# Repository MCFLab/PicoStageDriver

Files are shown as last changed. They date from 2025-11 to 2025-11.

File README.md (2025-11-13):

# Welcome to the Pico Stage Driver Project

The **Pico Stage Driver Project** is an open-source development of a low-cost, open-source controller design that drives several stepper motors and implements important safety features, such as monitoring of mechanical limit switches, stall detection, and protective software limits. If rotational encoders in the motors or linear encoders on the stages are available, the controller can monitor the stage position and correct it in a feedback loop. The stages can be controlled with serial commands via USB, or optionally from a remote control box that incorporates a joystick for real-time multi-axis speed control, rotary dials for fine axis positioning, and a display to indicate the stage positions. To ease adoption, we provide driver libraries in Python and C, a driver for the commonly used microscopy control software µManager, and an example graphical user interface for calibration and testing.

## Content

A paper describing the design and implementation is published here:

Mathias S. Fischer, David Grass, and Martin C. Fischer, "Modular multi-axis stepper motor driver with remote control for use in microscopy," [arXiv:2511.09456](https://doi.org/10.48550/arXiv.2511.09456) (2025).

Here we provide the [Bill of Materials](BOM.md), [Assembly Instructions](Assembly.md), and more detailed [Calibration Instructions](Calibration.md) than contained in the publication.

The [Mechanical Drawings](MechanicalDrawings/README.md) and [Software](Software/README.md) are in their respective subdirectories.

## Contributing

We welcome your contributions with [pull-requests](https://github.com/MCFLab/PicoStageDriver/pulls) and [issues suggesting further improvement](https://github.com/MCFLab/PicoStageDriver/issues)!

## License

This work is licensed under the
[GNU General Public License Version 3](https://www.gnu.org/licenses/gpl-3.0.en.html).

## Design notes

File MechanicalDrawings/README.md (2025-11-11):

# Mechanical Drawings

## Motor Controller

For the motor controller, we used an aluminum enclosure (Hammond 1455U2801, see BOM). On the front, we need holes for the USB cable to the Pico, the power switch, and two LEDs. On the back we mounted two rows of 9-pin Sub-D connectors for the motors and encoder/limit switches, the power connector jack, and the connector for the cable to the remote controller. We used a waterjet to cut the holes, using the "Motor Controller Front Panel" and "Motor Controller Back Panel" design files (supplied as Fusion 360 and STEP files). The cable connector is screwed to a 3D-printed adapter piece "RJ45Adapter", which we then glued to the inside of the back plate of the case.

## Remote Controller

The components for the remote controller are mounted in a 3D-printed case, consisting of a top shell and a bottom plate. For modularity, we designed the top shell as an assembly, which contains the shell and inserts for the joystick, the display, and motor controller cable connector. All of the shell components are attached with small #2 self-tapping screws. The encoders and the sensitivity potentiometer have threads and nuts and are fitted into the corresponding holes.

Note that the mounting holes for these components can differ between manufacturers and the dimensions might need adjustments.

We provide the Autodesk Inventor files and STEP files for the remote controller enclosure:

- Inventor:
  - "Top Assembly" (incorporating "RemoteControllerTop", "RJ45Insert", "JoystickInsert", and "DisplayInsert")
  - "RemoteControllerBottom"
- STEP
  - "Top Assembly"
  - "RemoteControllerBottom"

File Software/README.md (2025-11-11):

# Software

We provide the required software to be loaded onto the Motor Controller Pico and, if used, the remote controller Pico. The attached stages can be controlled either through the remote controller (if used) or via serial commands over USB (see the [detailed list of commands](CommandList.md)).

We also offer a driver package to interface with the Pico Stage Driver both in C and in Python, as well as simple graphical user interfaces utilizing these drivers. In addition, we implemented a rudimentary version of a driver for the popular microscopy control software [µManager](https://micro-manager.org/).

We provide basic [installation instructions](SoftwareInstallation.md) for all of the software provided.

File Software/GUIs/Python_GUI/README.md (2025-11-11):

# Stage Driver GUI

Small Tkinter GUI used to interact with PicoStage hardware. The
repository contains a lightweight MVC split: `stage_driver_view` for the
UI, `stage_driver_controller` for logic and `picostage` (external) for
hardware access.

What is included

- `panel_controls.py`, `status_panel.py`, `input_history_panel.py` — UI
  widgets and small controls.
- `stage_driver_view.py` — the main application window (Panel).
- `stage_driver_controller.py` — controller that wires the Panel to the
  PicoStage backend.
- `logging_texthandler.py` — helper that routes logging messages to the
  UI.

Quick start (development)

1. Create or activate a Python environment (this project was developed
   with Python 3.8+).

2. Run the GUI (requires the PicoStage package and hardware or a mock):

```powershell
py -3 main.py
```

Notes

- The GUI code uses tkinter widgets; tests instantiate widgets headless
  (no mainloop) and should run on systems with tkinter available.
- If your environment does not have `py` launcher, use your `python`
  executable instead.

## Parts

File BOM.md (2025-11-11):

# Bill of Materials

Note: Prices are approximate as of Nov 2025

## Motor Controller

| **Component** | **Number** | **Cost / unit** | **Source** | **Part number** | **Link** |
|----------|------|------|-------|--------|-------------------------------------|
| Microcontroller | 1 | \$5 | Raspberry Pi | Pico 2 | <https://www.raspberrypi.com/products/raspberry-pi-pico-2/> |
| TMC eval boards | 1-4 | \$68 | Analog Devices | TMC5240-EVAL | <https://www.analog.com/en/products/tmc5240.html> |
| Box | 1 | \$50 | Hammond | 1455U2801 | <https://www.newark.com/hammond/1455u2801/enclosure-multipurpose-extruded/dp/31AJ8269> |
| Power switch | 1 | \<\$1 | E-Switch | RA1113112R | <https://www.digikey.com/en/products/detail/e-switch/RA1113112R/3778055> |
| Power Jack | 1 | \$2 | MPD | EJ501B | <https://www.digikey.com/en/products/detail/mpd-memory-protection-devices/EJ501B/2439533> |
| Sub-D conn (female) | 1-4 | \<\$1 | various | A-DF 09 LL/Z | <https://www.digikey.com/en/products/detail/assmann-wsw-components/A-DF-09-LL-Z/5051922> |
| Sub-D conn (male) | 1-4 | \<\$1 | various | A-DS 09 LL/Z | <https://www.digikey.com/en/products/detail/assmann-wsw-components/A-DS-09-LL-Z/1241781> |
| Sub-D jack screws | 2-8 | \<\$1 | various | 4750-3 | <https://www.digikey.com/en/products/detail/raf-electronic-hardware/4750-3/7681452> |
| Protoboard | 1 | \$5 | Adafruit | 1609 | <https://www.adafruit.com/product/1609> |
| Headers for TMC board | 1-4 | \<\$1 | various | 10129381-950002BLF | <https://www.digikey.com/en/products/detail/amphenol-cs-fci/10129381-950002BLF/7916116> |
| RJ Jack | 1 | \$3 | Same Sky | CRJ068-1-SMT | <https://www.digikey.com/en/products/detail/same-sky-formerly-cui-devices/CRJ068-1-SMT/14322791> |
| Screw terminals | 2 | \$1 | Adels-Contact | 230/ 5 DS | <https://www.digikey.com/en/products/detail/adels-contact/230-5-DS/9998591> |
| 5-pin wire connectors (5-pack) | 1 | \$8 | Fielect |  | <https://www.amazon.com/dp/B0819PX1GY/> |
|  |  |  |  |  |  |

## Remote Controller

| **Component** | **Number** | **Cost / unit** | **Source** | **Part number** | **Link** |
|----------|------|-----|-------|--------|-------------------------------------|
| Microcontroller | 1 | \$5 | Raspberry Pi | Pico 2 | <https://www.raspberrypi.com/products/raspberry-pi-pico-2/> |
| Protoboard | 1 | \$5 | Adafruit | 1609 | <https://www.adafruit.com/product/1609> |
| RJ Jack | 1 | \$3 | Same Sky | CRJ068-1-SMT | <https://www.digikey.com/en/products/detail/same-sky-formerly-cui-devices/CRJ068-1-SMT/14322791> |
| Joystick | 1 | \$6 | Adafruit | 512 | <https://www.adafruit.com/product/512> |
| Rotary dial encoders | 1-4 | \$2 | various | KY-040 | <https://www.amazon.com/dp/B0D2TVTC75/> |
| Potentiometer | 1 | \$1 | various |  | <https://www.digikey.com/en/products/detail/tt-electronics-bi/P110KH1-0F15BR10K/2408866> |
| Knob for pot | 1 | \<\$1 | various |  | <https://www.digikey.com/en/products/detail/same-sky-formerly-cui-devices/SPK-016C/26004447> |
| Display | 1 | \$3 | various |  | <https://www.amazon.com/dp/B0BFD4X6YV/> |
| Protection diode | 1 | \<\$1 | various | 1N5817 | <https://www.digikey.com/en/products/detail/smc-diode-solutions/1N5817/21705460> |
|  |  |  |  |  |  |

## Various parts/supplies

For the assembly of the motor and remote controller, various small
electronics components and supplies are required, but these likely found
in any well-stocked electronics bench:

- Board spacers

- A selection of screws

- Wire of various gauges and colors

- Heat shrink tubing

- Small male and female headers

- LEDs

- Power supply: We used a spare laptop power supply, but this can
  readily be found at any electronics retailer for about \$10, depending
  on the voltage and current rating.

- Connector cable: We used a spare ethernet cord to connect the remote
  to the motor controller.

Because of the varied mounting holes for the joystick, rotary dial
encoders, and display, we decided to design and 3d-printed a custom
enclosure to house the components for the remote controller. We also
printed custom knobs for the rotary dial encoders.

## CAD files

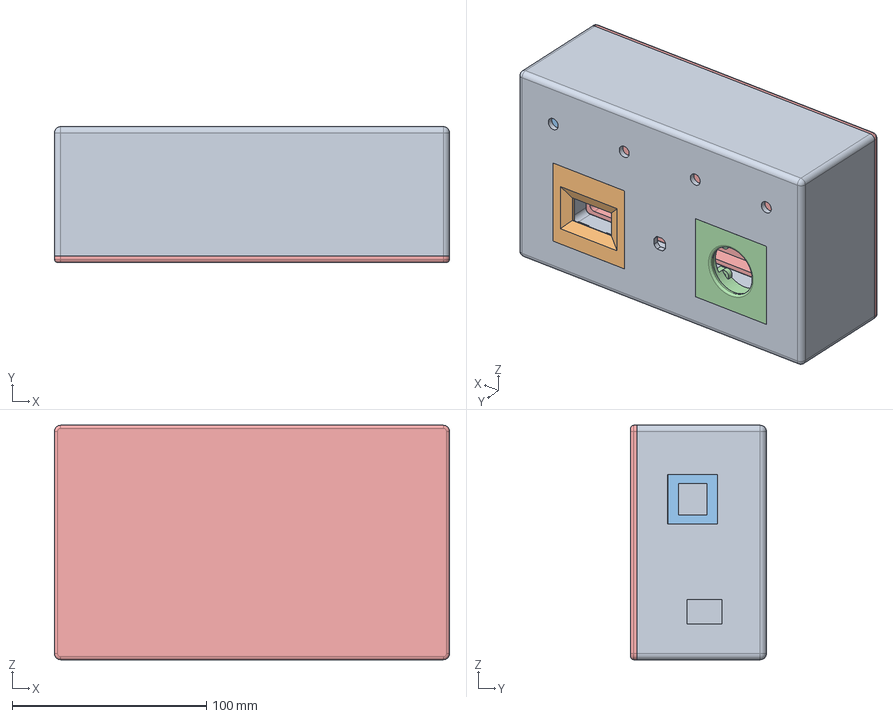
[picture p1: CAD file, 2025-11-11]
MechanicalDrawings/Top Assembly.step
203.2 x 69.9 x 120.7 mm
RemoteControllerTop
DisplayInsert
RJ45Insert
JoystickInsert
RemoteControllerBottom

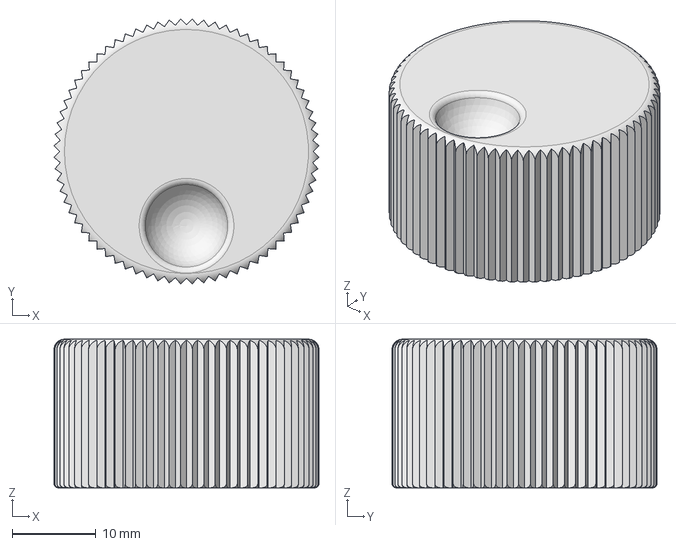
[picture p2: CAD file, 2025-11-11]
MechanicalDrawings/Encoder Knob.step
31.7 x 31.7 x 17.8 mm

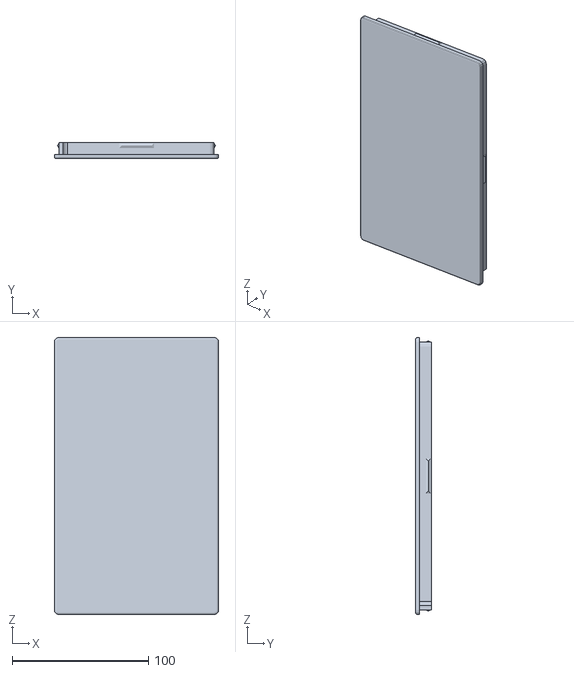
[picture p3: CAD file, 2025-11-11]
MechanicalDrawings/RemoteControllerBottom.stl
120.7 x 12.1 x 203.2

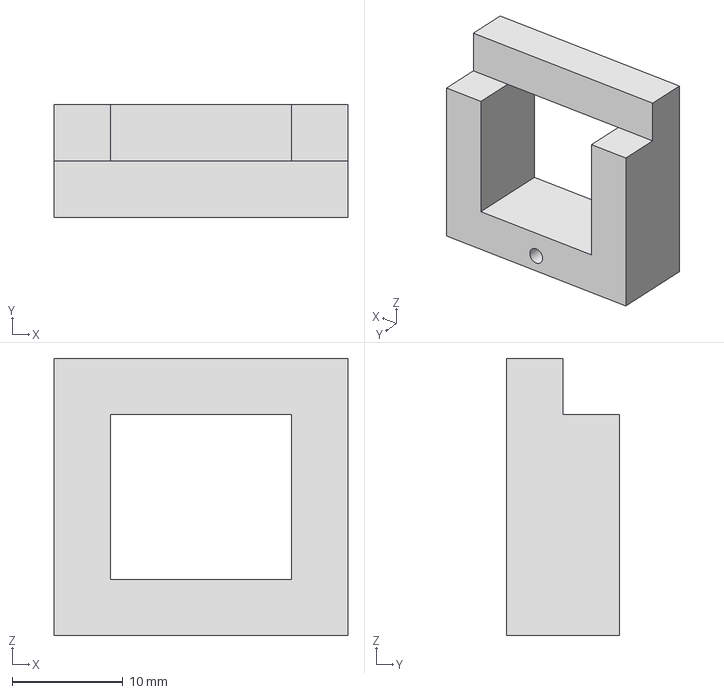
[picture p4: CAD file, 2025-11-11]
MechanicalDrawings/RJ45Adapter.step
26.5 x 10.2 x 25.0 mm

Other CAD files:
MechanicalDrawings/Motor Controller Front Panel.step
MechanicalDrawings/Motor Controller Back Panel.step
MechanicalDrawings/DisplayInsert.ipt
MechanicalDrawings/Encoder Knob.ipt
MechanicalDrawings/Encoder Knob.stl
MechanicalDrawings/JoystickInsert.ipt
MechanicalDrawings/Motor Controller Back Panel.f3d
MechanicalDrawings/Motor Controller Front Panel.f3d
MechanicalDrawings/RJ45Adapter.ipt
MechanicalDrawings/RJ45Adapter.stl
MechanicalDrawings/RJ45Insert.ipt
MechanicalDrawings/RemoteControllerBottom.ipt
MechanicalDrawings/RemoteControllerTop.ipt
MechanicalDrawings/Top Assembly.iam
MechanicalDrawings/Top Assembly.stl

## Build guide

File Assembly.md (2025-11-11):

# Assembly Instructions

## Motor controller

### Enclosure prep

1. Lay out the TMC boards and the protoboard in the box. Make sure to
   leave room for the screw connectors sticking out from the TMC
   boards. Also leave enough room for the switch and LEDs in the front
   but remember that the USB cable sticks through the front panel to
   the Pico, so don’t mount the Pico too far back.

1. Mark the mounting holes with a pencil. Drill the holes, screw in the
   board spacers from the bottom (we used 4-40 spacers). Test to make
   sure the board fits on the spaces, but don’t’ mount them yet. Drill
   an extra hole for the GND to case connection later.

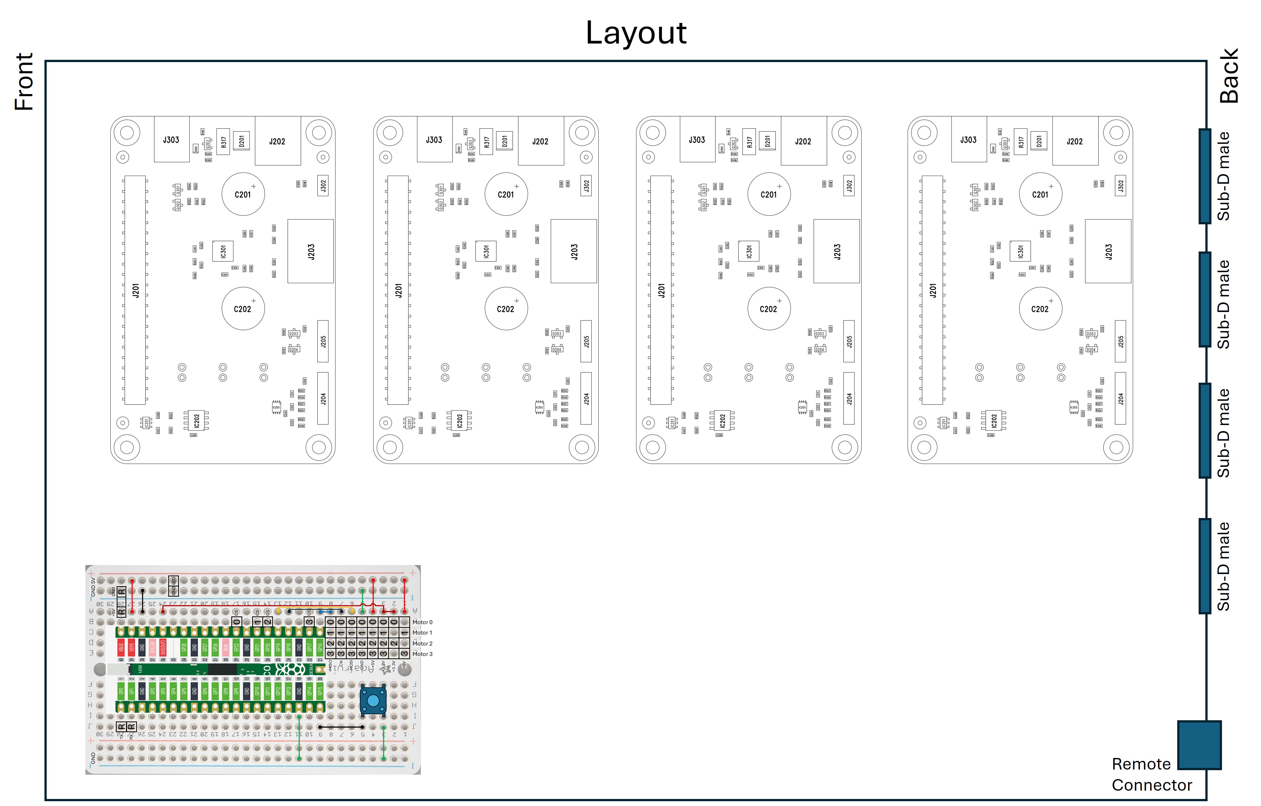
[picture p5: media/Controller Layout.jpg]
   

1. Glue on some rubber pads on the bottom so the screws don’t scratch
   up whatever the box is standing on.

1. With the tool of your choice, cut out the holes to mount the
   components in the front and back panels. We provide the design files
   for our layout for use with an automated tool (we used a waterjet),
   but a CNC mill, Dremel tool, or hand tools will work.

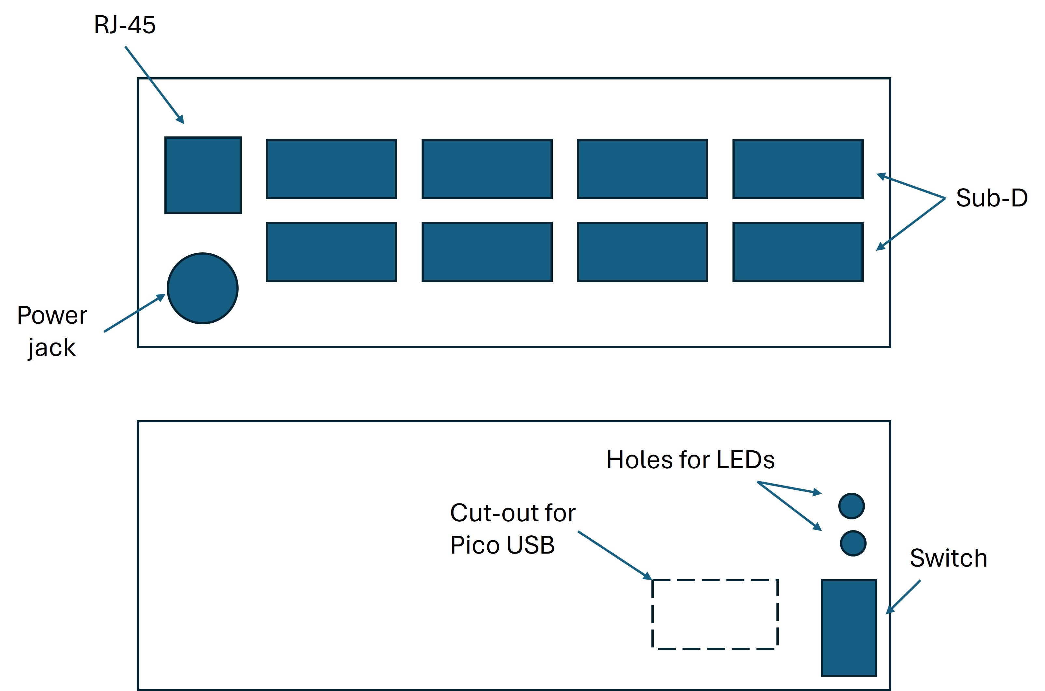
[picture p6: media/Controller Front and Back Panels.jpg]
   

1. Make sure the USB cutout lines up with the connector of the Pico
   when mounted on the spacers.

### Power and motor layer

1. Prep the motor cable from the TMC board to the motor connector on
   the back of the box. As connectors we used sub-D connectors, but
   that depends on your stages/cables. Use wires that can carry the
   motor current (we used 20 gauge stranded). Twist the A1 and A2 wires
   and the B1 and B2 wires, solder one side to the motor connector in
   the back of the box. Cut to length, mount the connector, and route
   the cable in the box. The other end of the cables goes in the screw
   connector of the TMC boards. Make sure the pinouts match!

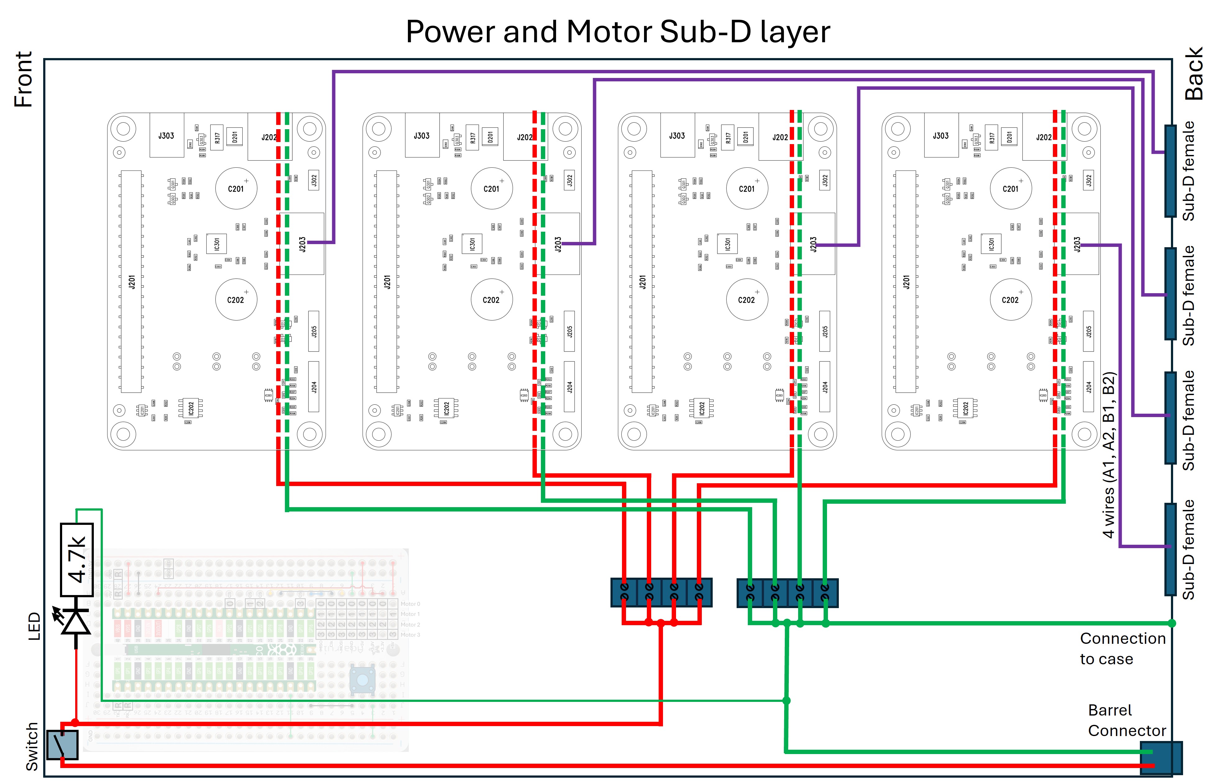
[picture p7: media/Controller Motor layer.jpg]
   

1. Mount the power jack (barrel connector), route the +V~M~ cable (we
   used a red 18 gauge wire) from the barrel to the switch (we used
   flat terminal connectors for the switch) and from there to the
   terminal strip. The GND cable goes to the terminal strip. At the
   terminal strip, branch out the wires.

1. From the terminal strip, one GND connection goes to the case for
   protection and shielding (we use a wire lug in a spare hole in the
   box).

1. One (thin) +V<sub>M</sub>/GND wire pair goes to the power led in the front.
   Use a resistor in series to limit the current. The resistor value
   depends on the supply voltage – we used a 4.7k resistor. Mount the
   LED (we used a mounting ring but still had to glue that in place).
   We put a connector in the wire pair so we could detach the LED when
   taking off the front panel.

1. Run a pair of twisted +V<sub>M</sub>/GND wires to each of the TMC boards. We
   ran the supply wires under the boards for convenience. The
   connectors on the board are screw connectors.

1. Mount the TMC boards on the spacers.

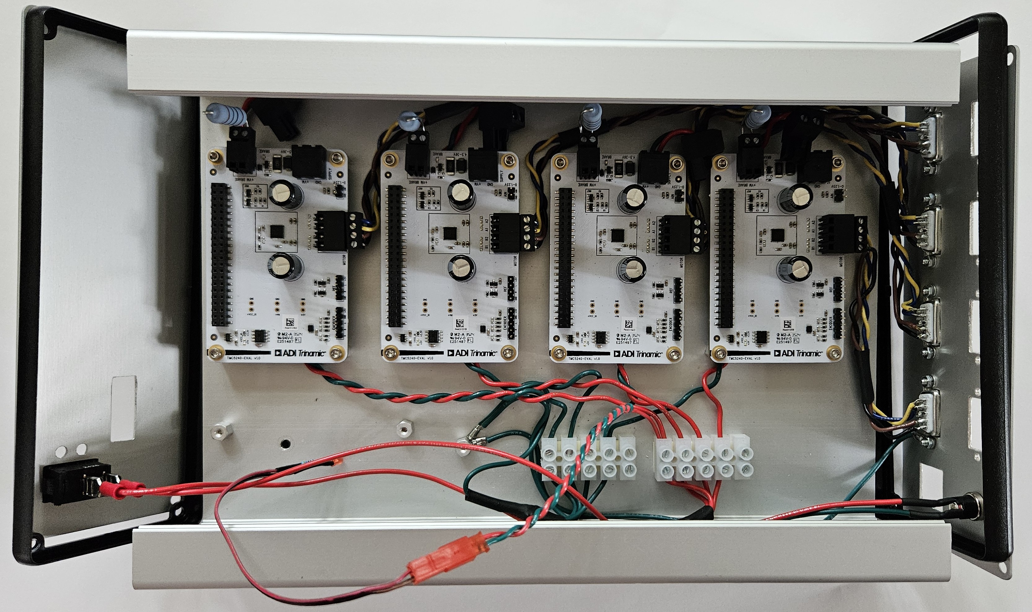
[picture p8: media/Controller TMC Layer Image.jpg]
   

### Pico protoboard

1. Here is the layout of the board:

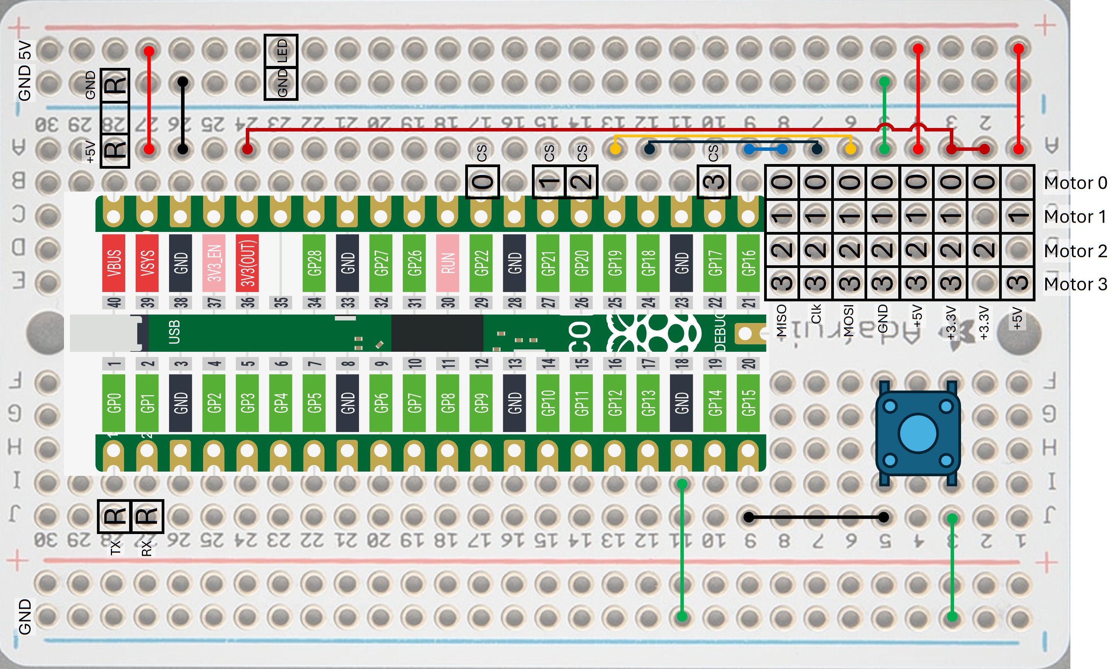
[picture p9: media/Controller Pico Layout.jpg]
   

1. Solder two rows of 20-pin female headers for the Pico.

1. Solder in the male headers (squares in the layout above):

   - 4 rows of 8-pin headers for the TMC connectors.

   - Individual pins for the CS, LED, remote power, and UART.

1. Solder in the “load default” push button

1. Solder in a few hookup wires according to the layout diagram.

1. Mount the protoboard on the spacers. If you use metallic spacers,
   when mounting the Pico protoboard on them, make sure they don’t
   short any connections underneath. If you are close to a connection,
   use a plastic washer.

### Control layer

1. Prep the cables from the TMC board to the encoder / limit switch
   connectors on the back of the box (we used sub-D connectors, but
   that depends on your stages/cables). For the TMC encoder connector
   side, we used prefabricated 5-pin Dupont connector cables. For the
   limit switch connectors, we used a row of female headers. Solder the
   other end of the cables into the sub-D connector. Double-check the
   pinouts!

1. Prep the TMC to Pico connectors. We used a 2-row male header for the
   TMC side. To reduce the number of wires, connect several of the pins
   right at the connector (see diagram below). There are a total of 8
   wires from the connector to the Pico protoboard. On the Pico side we
   used DuPont headers. Some of these are (again) prefab 5-pin
   connectorized cables, the others are individual connectors. You can
   put on Dupont connectors yourself with a crimp tool, but it’s easier
   to use a handful of connectorized hookup cables.

   <table>
       <tr>
           <td>
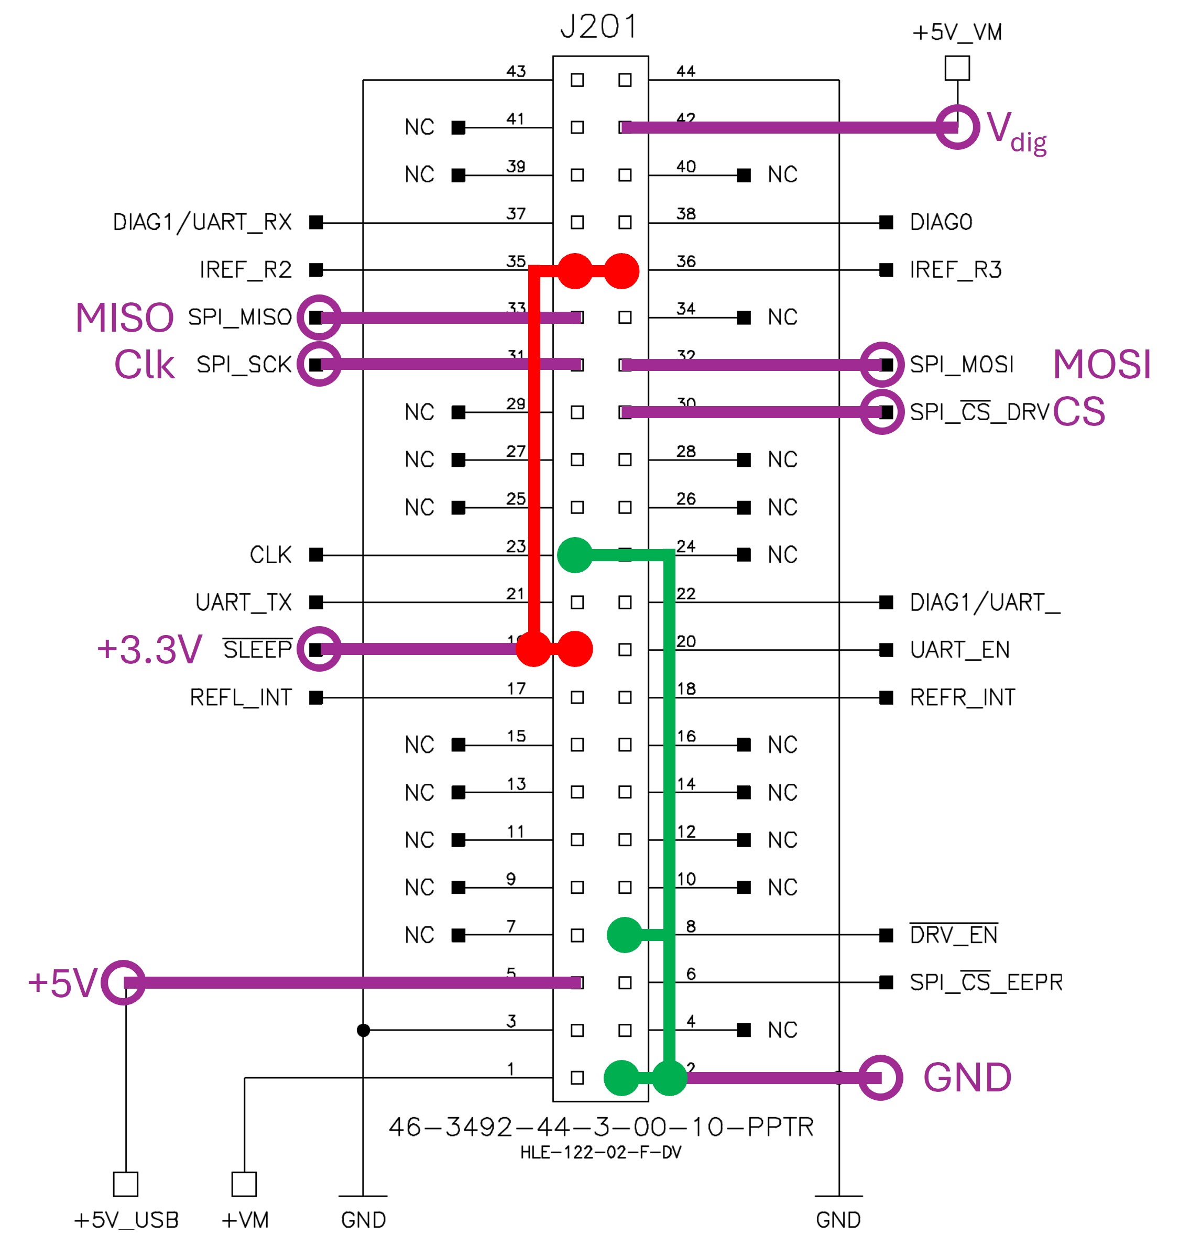
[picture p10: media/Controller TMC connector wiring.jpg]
             
           </td>
           <td>
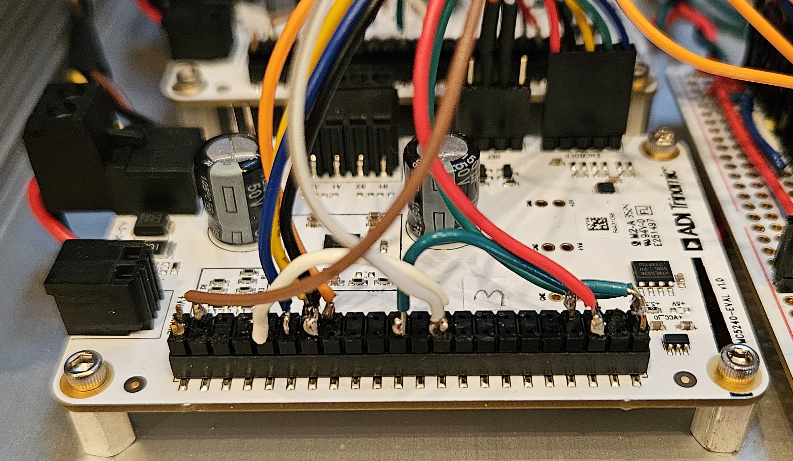
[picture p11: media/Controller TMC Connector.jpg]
             
           </td>
       </tr>
   </table>

1. Prep the RJ-45 jack cables. One side gets soldered into the jack,
   the other gets Dupont connectors. Make sure the TX and RX connectors
   are mapped to lines that are twisted with ground. We used this
   assignment:

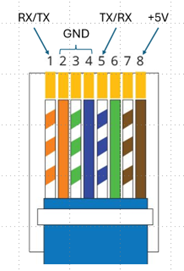
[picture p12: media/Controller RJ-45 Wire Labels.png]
   

1. Mount the jack. We screwed the Jack into a plastic adapter and glued
   the adapter to the back plate.

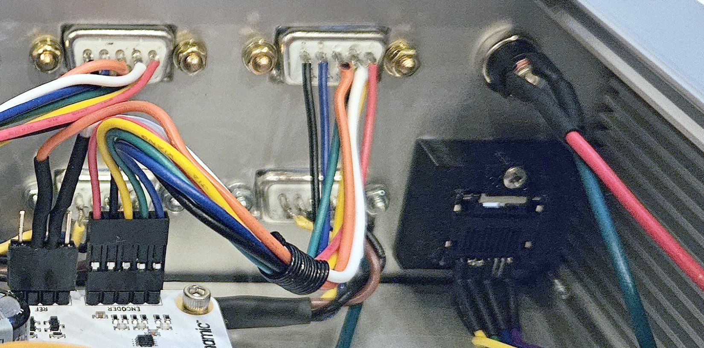
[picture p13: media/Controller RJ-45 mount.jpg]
   

1. For the Pico power LED, use a series resistor (\~1k) to limit the
   current. Use Dupont connectors on the Pico side.

1. Connect the LED (2 pins), the RJ-45 jack (4 pins).

1. Connect the TMC connectors (8 pins each). For the V<sub>dig</sub> connector,
   choose a pin from the 3.3V or 5V line of the Pico protoboard,
   depending on the required voltage of your encoder. When pushing in
   the TMC connectors, make sure all pins are well seated, since
   soldering tends to loosen the pins in the connector. Triple check
   the connections!

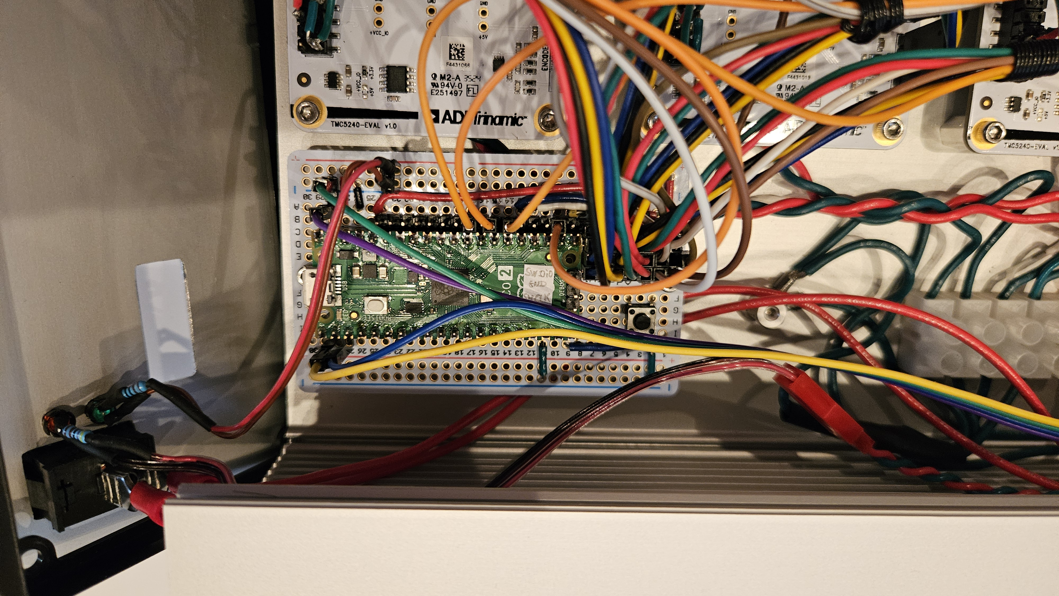
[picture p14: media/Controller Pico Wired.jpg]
   

1. If required (for larger motors) install a brake resistor (see TMC
   datasheet). **Careful**: At some point during software debugging of
   the SPI communication, the TMC chips ended up in a mode that
   continually activated the overvoltage transistor (visible by the red
   LED on the TMC board). This seriously overheated the brake resistor!
   This should no longer occur, but we never ended up installing the
   brake resistors.

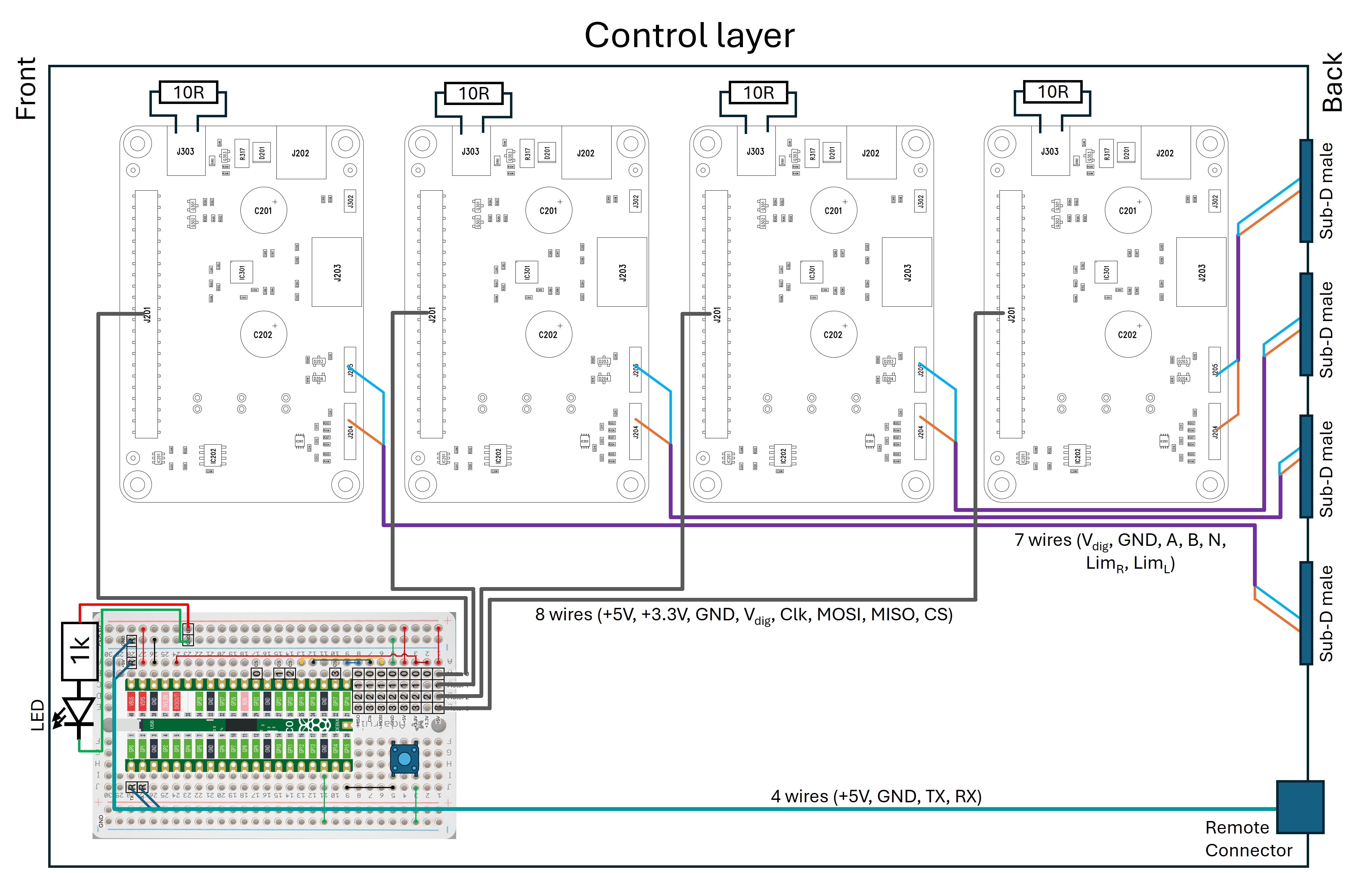
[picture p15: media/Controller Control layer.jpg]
   

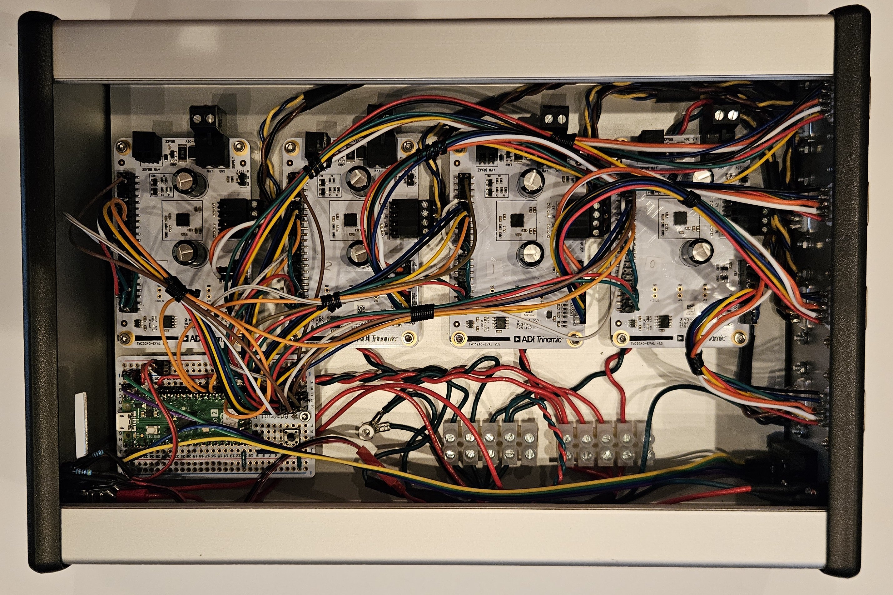
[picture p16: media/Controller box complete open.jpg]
   

Congratulations, you concluded the motor control assembly! We recommend
operating the controller for a while without lid (see our comment on the
brake resistor!) so you can see what’s going on in there. Also,
initially you might need access to the default load button (in the next
version, this button could be placed in a more accessible location,
maybe where it can be reached through the USB cutout).

## Remote controller

### Pico protoboard

1. Here is the layout of the board:

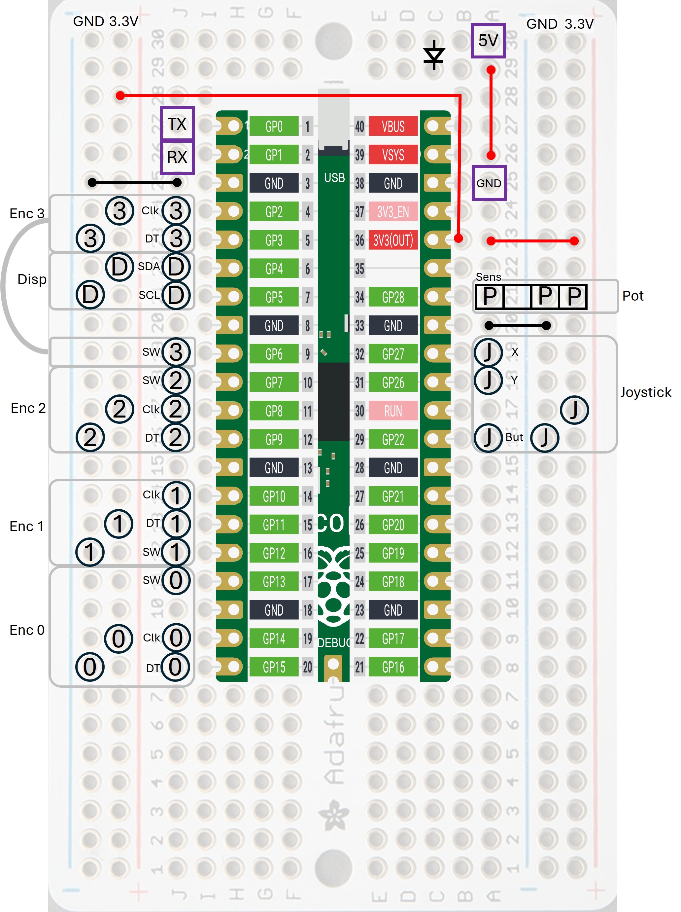
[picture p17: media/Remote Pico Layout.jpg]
A screenshot of a computer AI-generated content may be incorrect.
   

1. Solder two rows of 20-pin female headers for the Pico.

1. Solder in the male headers (squares in the layout above):

   - 3 pins for the potentiometer (Sens, GND, and 3.3V)

   - 4 pins for the RJ-45 jack (GND, supply voltage for the pico, TX,
      and RX)

1. Solder in the protection diode for the Pico supply voltage as
   indicated.

1. Solder in a few hookup wires according to the layout diagram.

1. Solder in sets of 5-pin prefab Dupont connector wires for the
   devices listed. Note that the wires in the connectors can be removed
   and rearranged to adhere to a common color scheme (if desired).

   - 4 encoders

   - 1 joystick

   - 1 display (only uses 4 of the 5 wires)

1. Solder the wires to the pot, the other end should be Dupont
   connectors.

1. Prep the RJ-45 jack cables. Use the same assignment as above.

1. Connect all these. Note that you change the direction of the
   sensitivity pot (clockwise/anticlockwise) by swapping the GND and
   3.3V pins. Also, the TX from the motor controller needs to go in the
   RX of the remote controller and vice versa.

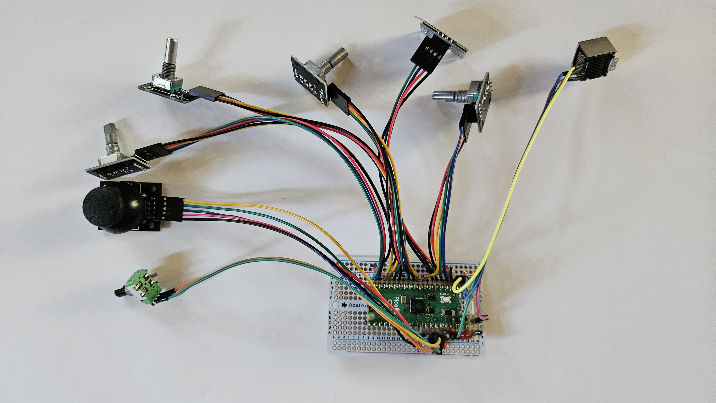
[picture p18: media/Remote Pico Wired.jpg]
   

1. Mount the RJ-45 jack, the display, the joystick, the encoders, and
   the pot.

1. 3D print the encoder knobs (or use other ones) and attach then to the encoders.

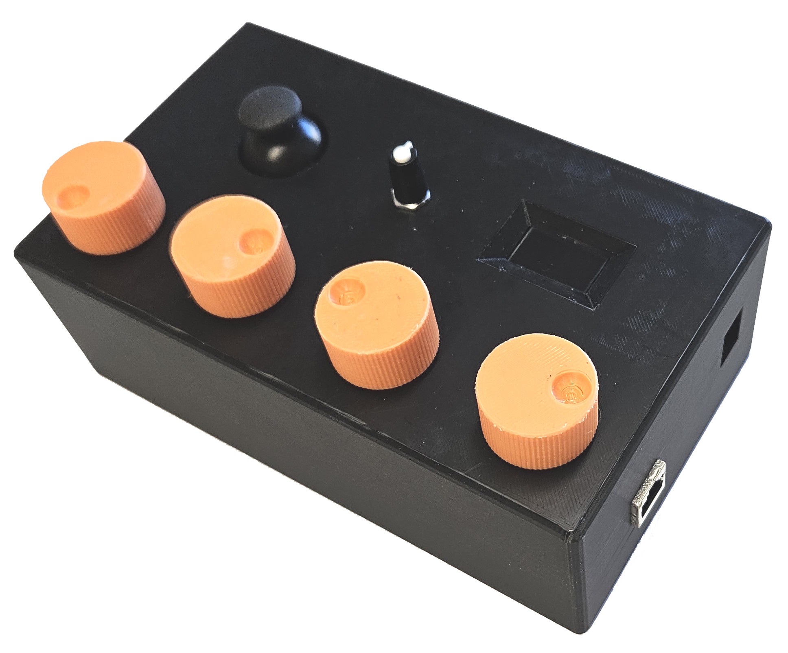
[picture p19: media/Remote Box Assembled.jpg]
   

Congratulations, you concluded the remote controller assembly! You can now attach it to the motor controller via a standard ethernet cable connected to the two RJ-45 jacks. You can connect the remote controller to a USB port for debugging, but that is optional. During normal operation it is powered from the motor controller (no extra configuration required).

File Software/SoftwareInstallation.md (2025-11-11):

# Software installation

## Building the Pico code

The motor and remote controller software can be built either with the
Arduino IDE or with Visual Studio Code and PlatformIO.

The Arduino IDE needs to be configured using the Earle Philhower
framework. This can be achieved by including
<https://github.com/earlephilhower/arduino-pico/releases/download/global/package_rp2040_index.json>
as an additional board manager URL in the Arduino IDE preference. In
addition, the driver for the display needs to be installed through the
library manger – search for “Adafruit SSD1306” and “Adafruit GFX” will
bring up the correct libraries for installation. After that, loading the
corresponding .ino file will also find the associated files. Once
“Raspberry Pi Pico 2” with the correct COM port number is selected, the
program is ready for building and flashing.

The VS code environment needs the PlatformIO extension to be installed.
Once installed, opening the folder with the platformio.ini file should
be all that is required. Make sure that the COM port listed in this file
reflects the correct port of the Pico.

## Libraries and GUI

### C library

The C library requires a VISA driver library (see the paper for links).
These are installer packages and should not require further
configuration. The library header file contains the function prototypes.

### Python library

The Python library also requires a VISA installation. We use the free
pyVISA and pyVISA-py packages. Since we use a serial connection,
pySerial is also required. We combined the Python library into a whl
file that contains a pre-built version of the Python package that can be
directly installed and which also includes the required dependencies. A
simple `pip install picostage-driver.whl` will do the trick.

### Python GUI and test scripts

The python GUI uses tkinter, which comes bundled with python
installations. For calibration, we wrote a Jupyter notebook with several
test scripts, which utilize the matplotlib, numpy, and pandas packages.

### µManager driver

Once validated by a few other groups, we intend to request a pull to incoporate
our driver in the µManager distribution.
For the time being,
to install the driver on a Win64 system, simply copy the file `mmgr_dal_PicoStageDriver.dll`
into the main µManager directory (e.g. `C:\Program Files\Micro-Manager-2.0`), adjust the
startup config file (see below), and start µManager.
Should this fail, a compilation is required (see the [instructions to set up the µManager environment](https://micro-manager.org/Building_MM_on_Windows)). The provided driver files
should be copied into a directory named
`PicoStageDriver\` in the `mmCoreAndDevices\DeviceAdapters\` directory
and the project should be built.

The µManager driver is based on the Arduino example by Nico Stuurman
(<https://micro-manager.org/Arduino>). This driver uses a Hub device, through
which the XY stage, the Z-stage, and an auxiliary Z-stage are
controlled. The stage driver can be set up with axis identifiers (see
"TypeAxis" below) that automatically identify the corresponding axes in
µManager. Ultimately, we will request inclusion of our driver into the
µManager repository, but for the time being, the compiled dll can be
copied into the program directory (both the dll and source are included
in the online repo). The hardware wizard will then recognize the
picostage driver and configure the device for inclusion. The axis
velocity and acceleration setting for each configures axis are read from
the controller Pico, but can be overridden with device parameters from
µManager. The only parameters not obtained from the controller are the
step sizes, which can be set as device properties, e.g.

```
Property,Pico-XYStage,StepSizeX [um],0.078125  
Property,Pico-XYStage,StepSizeY [um],0.078125  
Property,Pico-ZStage,StepSize [um],0.03125  
```

Note that requesting remote access from the remote controller will
prevent stage control from the computer, i.e. µManager. This behavior is
by design to prevent accidental (and undetected) motion during a
computer acquisition. For µManager to regain control of the stages, the
device parameter "IsRemoteControlled" can be re-set to 0.

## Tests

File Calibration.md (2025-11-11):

# Calibration

The settings of the motor parameters can be adjusted and calibrated
using the finished stage driver. For programming and debugging we
utilized the TMC Landungbrücke, which is a USB interface that comes with
the TMC5240-EVAL-KIT (not the TMC5240-EVAL). This interface allows full
control of the TMC board with the TMC-IDE software, which proved helpful
for understanding the TMC features. For adapting our stage driver to
specific motors, it is not required.

## Motor settings

### Mode parameters

MP_MMIC (“ModeMicroStep”) determines the number of microsteps per full
step and corresponds to the MRES field in the CHOPCONF register (number
of microsteps per full step is 2\^MRES). It ranges from 0 (256
microsteps per full step) to 8 (no microstepping). If an encoder is
present, this should be set such that the motor step size approximates
the encoder step size (fine tuning can be done with MP_ECON).

MP_MINV ("ModeInvDir") is a flag to invert (1) the motor direction. It
corresponds to the SHAFT field in the GCONF register.

MP_MTOF ("ModeTOff") corresponds to the TOFF field in the CHOPCONF
register. This parameter is used to enable or disable the motor. A value
of 0 disables the motor, a value between 1 and 15 enables it. For our
motor configuration, any non-zero value will enable the motor, we chose
a default value of 5.

MP_MSGE ("ModeSGEnable") is a flag to enable (1) or disable (0) the
StallGuard2 feature of the TMC. It corresponds to the SG_STOP field in
the RAMP_STAT register. MP_MTCT ("ModeTCT") determines the minimum
velocity at which the stall guard feature is enabled (it will not work
at low speeds) and corresponds to the TCOOLTHRS register. The threshold
velocity could be set slightly below the usual operating velocity $v$.
The value is then set as
$\text{TCOOLTHRS} \approx 1.1*2^{24}*2^{- \text{MRES}}/v$ , where $v$ is
the set velocity in MS/sec and MRES is the microstep factor (see above).
MP_MSGT ("ModeSGT") is a gain factor that determines the sensitivity for
stall guard detection and corresponds to the SGT field in the COOLCONF
register. The range is -64 to +63 (0 is default); higher values make
StallGuard less sensitive and requires more torque to indicate a stall.
This value should be adjusted empirically by running the motor at the
set speed and manually blocking motor rotation until a stall is
registered. Note that for a motor stage with a fine pitch spindle,
especially when the motor is geared, the StallGuard mechanism may not
reliably detect a stall. In this case, setting up encoder deviation
monitoring is more reliable.

### Motor currents

See the section “Current setting” in the TMC manual for a quick
configuration guide. In short, the parameters listed here determine the
current applied during motor motion (“run”) and standstill (“hold”). The
overall current range can be set by hardware configuration through a
resistor attached to the IREF on the TMC chip. On our eval board, we can
choose from a set of discrete built-in resistors (see the TMC Eval data
sheet). We pull IREF_R2 and IREF_R3 on the TMC connector to high (3.3V)
to set the highest current range (the max range is then limited by the
following scale parameters).

MP_CRAN ("CurrRange") corresponds to the field CURRENT_RANGE of register
DRV_CONF and determines the overall range of currents. Values are 0 -\>
max current of 1A, 1 -\> 2A, 2 or 3 -\> 3A.

MP_CSCA ("CurrScaler") corresponds to the GLOBAL_SCALER register and
linearly adjusts the overall currents. The range is 32 to 255 (max);
however, the manual recommends values \>128.

MP_CRUN ("CurrRun") and MP_CHOL (CurrHold") correspond to the fields
IRUN and IHOLD in register IHOLD_IRUN, respectively. It linearly scales
the run and hold currents in the range of 0 to 32 (max). IRUN between 16
and 31 is recommended for best microstep performance.

### Speed settings

MP_RSEV ("RateSetVelocity") is the set velocity for positioning
commands, and MP_RMXV ("RateMaxVelocity") is a maximum allowed velocity
for positioning or velocity commands. MP_RSEA ("RateSetAcc") and MP_RMXA
("RateMaxAcc") are the same but for acceleration. Units are MS/sec and
MS/sec^2^, respectively.

### Homing settings

HMOD ("HomingMode") sets the mode used to search for the reference
position. A value of 0 disables homing, 1 uses the limit switches, and 2
uses the encoder index position. Note that since we did not have an
encoder with an index, the “2” mode is untested. MP_HDIR
("HomingDirection") sets the homing direction: -1 searches in the
negative direction, i.e. for the negative (“left”) limit switch or the
encoder index, +1 towards in the positive direction (right limit switch)
or index. Note that to use the limit switch search, the switch in the
corresponding direction needs to be anabled. MP_HVEL ("HomingVelocity")
determines the velocity for home searches, MP_HSST ("HomingSoftStop") is
a flag whether the motor should do a soft stop (1) at the set
acceleration or a hard stop (0) when a homing position is reached. In
the soft stop case, the homing reference is adjusted to account for the
slow deceleration. MP_HNEV ("HomingIndexEvent") corresponds to the field
pos_neg_edge of register ENCMODE and determines what kind of polarity to
use for the index search.

### Switch settings

MP_SLEN ("SwitchLeftEnable") and MP_SREN ("SwitchRightEnable") are flags
to indicate the presence (1) or absence (0) of left/right limit
switches. MP_SLPO ("SwitchLeftPolarity") and MP_SRPO
("SwitchRightPolarity ") are flags to indicate the polarity of the
left/right switches (0: non-inverted, a high level on the switch stops
the motor; 1: inverted, a low level on the switch stops the motor).
MP_SSWP ("SwitchSwap"), if set to 1, swaps the role of the left and
right switch. These parameters correspond to the STOP_L_ENABLE,
STOP_R_ENABLE, POL_STOP_L, POL_STOP_R, and SWAP_LR fields of the SW_MODE
register, respectively.

### Limits settings

MP_LLEN ("LimLeftEnable") and MP_LREN ("LimRightEnable") are flags to
indicate whether the left/right software (“virtual”) limits are enabled.
These parameters correspond to the EN_VIRTUAL_STOP_L and
EN_VIRTUAL_STOP_R fields of the SW_MODE register, respectively. The
actual left and right limits are determined by MP_LLPS
("LimLeftPosition") and MP_LRPS ("LimRightPosition"), which correspond
to the VIRTUAL_STOP_L and VIRTUAL_STOP_R registers. MP_LENC
("LimEncoder") determines whether the motor position (0) or the encoder
position (1) is used to determine the virtual limits. This corresponds
to the VIRTUAL_STOP_ENC field of the SW_MODE register.

### Encoder settings

MP_ECON ("EncConstant") is the encoder constant, which in turn
determines the number of steps the TMC adds for every encoder count
received. This parameter corresponds to the ENC_CONST register. The
constant reflects the ratio $r$ = microsteps / encoder count. The ratio
does not have to be an integer but needs to be sent to the register as a
signed integer. The TMC has a specific way to encode the fraction $r$ as
the ENC_CONST, which is not the usual floating point representation. For
a detailed description, please refer to the TMC datasheet. Here we
utilize the decimal representation. To calculate the encoder constant we
split $r$ into its integer part $r_{i}$ and fractional part $r_{f}$.
ENC_CONST can then calculated as:

$$
{\mathrm{ENC}}_{-}{\mathrm{CONST}} =
\begin{cases}
2^{16} \ r_i + 10{,}000 \ r_f & \text{if } r > 0 \\
2^{16} \ (2^{16} - r_i - 1) + 10{,}000\ (1 - r_f) & \text{if } r < 0
\end{cases}
$$

Furthermore, if $r$ is negative, this constant needs to be converted
into a 32-bit signed format, which can be achieved by:

$${{\mathrm{ENC}}_{-}{\mathrm{CONST}}}_{\text{signed}} = {\mathrm{ENC}}_{-}{\mathrm{CONST}} - 2^{32}$$

Since this method is less-than-intuitive, we provided a helper python
function for this conversion in the repository.

MP_EDEV ("EncDeviation") is the maximum allowed deviation between
encoder reading and motor position before a following error is raised.
Set this to 0 to disable deviation check. This parameter corresponds to
the ENC_DEVIATION register.

MP_EMAX ("EncLoopMax") sets the position operation mode. A value of 1
(one try to get to the desired position) corresponds to an open-loop
mode. A value \>1 sets the “open loop with pull-ins” mode and sets the
maximum number of pull-in tries. A value of 0 sets the “closed-loop”
mode, where the motor continuously readjusts according to the encoder
position.

MP_ETOL ("EncLoopTolerance") sets the tolerance window for “Open-loop
with pull ins” and “Closed-loop” operation modes.

If there is a large deviation between the TMC motor position and the
encoder position, a small incremental movement would result in a first
step of the size of this deviation before it is pulled back to the
target position. To avoid this, we can set MP_ERST ("EncResetXafterCL")
to 1, for which the actual and target position register of the TMC are
set to the encoder position after a pull-in or closed loop motion
completes.

### Device and axis types

MP_TDEV (TypeDevice) determines whether a TMC board of the respective
board number is actually attached to the Pico. A value of 0 indicates no
TMC is attached – any attempt to send commands to this board will result
in an error. A value of 1 simulates a board – positioning and velocity
commands still work, but don’t control a motor. This mode is useful for
debugging. Finally, a value of 2 indicates a TMC board present.

MP_TAXI ("TypeAxis") is intended for use with µManager and serves to
identify what kind of axis the channel corresponds to. The values are: 0
is an undefined axis, 1 is an X-axis, 2 a Y-axis, 3 a Z-Axis, and 4 an
auxiliary axis. When set, µManager can automatically assign the channels
to the corresponding devices (XY-Stage, Z-Stage, or Aux-Stage).

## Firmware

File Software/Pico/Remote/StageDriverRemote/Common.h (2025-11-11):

#define MAX_NUM_MOTORS                      4 // maximum number of motors (at most 4)
#define COMMON_ADC_RESOLUTION               10 // bit depth of the ADC (Joystick and SensAdjust)
#define ADC_AVERAGING_BASE                  6 // average 2^6=64 samples, ADC_RES + BASE must be <= 16
#define ADC_UPDATE_INTERVAL_MS              4 // ADC sampling interval in ms for averaging

#define INPUT_MODE_CHECK_INTERVAL_MS        10 // check interval for joystick/encoder switchover in ms
#define INPUT_MODE_DEBOUNCE_TIMEOUT_MS      300 // dbounce timeout for switching input mode in ms

#define ENCODER_CH0_PIN_ENCA                D14   // pin number (GPxx) for signal A (-1 for unused); B is the next pin
#define ENCODER_CH1_PIN_ENCA                D10
#define ENCODER_CH2_PIN_ENCA                D8
#define ENCODER_CH3_PIN_ENCA                D2
#define ENCODER_CH0_PIN_BUTTON              D13 // pin number (GPxx) for the button of the encoder (-1 for unused)
#define ENCODER_CH1_PIN_BUTTON              D12
#define ENCODER_CH2_PIN_BUTTON              D7
#define ENCODER_CH3_PIN_BUTTON              D6

#define JOYSTICK_CH0_PIN_ADC                A0 // Analog ADC0 (set to -1 if not used)
#define JOYSTICK_CH1_PIN_ADC                A1 // Analog ADC1 (set to -1 if not used)
#define JOYSTICK_CH2_PIN_ADC                -1 // not used
#define JOYSTICK_CH3_PIN_ADC                -1 // not used
#define JOYSTICK_CH0_PIN_BUTTON             D22 // GPIO 22 (set to -1 if not used)
#define JOYSTICK_CH1_PIN_BUTTON             D22 // same as Ch0
#define JOYSTICK_CH2_PIN_BUTTON             -1 // not used
#define JOYSTICK_CH3_PIN_BUTTON             -1 // not used

#define SENSADJUST_PIN_ADC                  A2 // Analog ADC2 (set to -1 if not used)

#define DISPLAY_PIN_SDA                     PIN_WIRE0_SDA // SDA pin, default is D4 (board pin 6) for the Pico 2
#define DISPLAY_PIN_SCL                     PIN_WIRE0_SCL // SCL pin, default is D5 (board pin 7) for the Pico 2
#define DISPLAY_I2C_ADDRESS                 0x3C
#define DISPLAY_SCREEN_WIDTH                128
#define DISPLAY_SCREEN_HEIGHT               64

#define UART_BAUDRATE                       921600
#define UART_PIN_TX                         PIN_SERIAL1_TX
#define UART_PIN_RX                         PIN_SERIAL1_RX

#define UART_BUFFER_SIZE                    1024
#define UART_SEND_INTERVAL_MS               20 // interval in ms for sending updates to the controller
#define UART_RECEIVE_INTERVAL_MS            10 // interval in ms for receiving updates from the controller

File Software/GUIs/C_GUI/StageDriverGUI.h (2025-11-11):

/**************************************************************************/
/* LabWindows/CVI User Interface Resource (UIR) Include File              */
/*                                                                        */
/* WARNING: Do not add to, delete from, or otherwise modify the contents  */
/*          of this include file.                                         */
/**************************************************************************/

#include <userint.h>

#ifdef __cplusplus
    extern "C" {
#endif

     /* Panels and Controls: */

#define  PAN_MAIN                         1
#define  PAN_MAIN_BUT_CLOSE               2       /* control type: command, callback function: cb_Close */
#define  PAN_MAIN_BUT_LOAD                3       /* control type: command, callback function: cb_FileLoad */
#define  PAN_MAIN_BUT_SAVE                4       /* control type: command, callback function: cb_FileSave */
#define  PAN_MAIN_BUT_REMOTE_GETPARAM     5       /* control type: command, callback function: cb_remoteParam */
#define  PAN_MAIN_BUT_REMOTE_SETPARAM     6       /* control type: command, callback function: cb_remoteParam */
#define  PAN_MAIN_BUT_MOTOR_GETPARAM      7       /* control type: command, callback function: cb_motorParam */
#define  PAN_MAIN_NUM_REMOTE_PARAM_VAL    8       /* control type: numeric, callback function: (none) */
#define  PAN_MAIN_BUT_MOTOR_SETPARAM      9       /* control type: command, callback function: cb_motorParam */
#define  PAN_MAIN_RNG_REMOTE_PARAM        10      /* control type: ring, callback function: (none) */
#define  PAN_MAIN_BOX_STATUS              11      /* control type: textBox, callback function: (none) */
#define  PAN_MAIN_NUM_MOTOR_PARAM_VAL     12      /* control type: numeric, callback function: (none) */
#define  PAN_MAIN_NUM_SETPOSITION         13      /* control type: numeric, callback function: cb_SetPosition */
#define  PAN_MAIN_NUM_POSITION            14      /* control type: numeric, callback function: cb_Position */
#define  PAN_MAIN_NUM_MOTOR               15      /* control type: numeric, callback function: (none) */
#define  PAN_MAIN_RNG_MOTOR_PARAM         16      /* control type: ring, callback function: (none) */
#define  PAN_MAIN_TEXTMSG                 17      /* control type: textMsg, callback function: (none) */
#define  PAN_MAIN_BUT_CONFIG              18      /* control type: command, callback function: cb_Config */
#define  PAN_MAIN_BUT_CHECKERROR          19      /* control type: command, callback function: cb_CheckError */
#define  PAN_MAIN_BUT_STOP                20      /* control type: command, callback function: cb_Stop */
#define  PAN_MAIN_BUT_DISABLE             21      /* control type: command, callback function: cb_Disable */
#define  PAN_MAIN_BUT_ENABLE              22      /* control type: command, callback function: cb_Enable */
#define  PAN_MAIN_BUT_CLEAR               23      /* control type: command, callback function: cb_Clear */
#define  PAN_MAIN_STR_DIRECTCOM           24      /* control type: string, callback function: cbDirectCommand */
#define  PAN_MAIN_LED_0                   25      /* control type: LED, callback function: (none) */
#define  PAN_MAIN_LED_1                   26      /* control type: LED, callback function: (none) */
#define  PAN_MAIN_LED_2                   27      /* control type: LED, callback function: (none) */
#define  PAN_MAIN_LED_3                   28      /* control type: LED, callback function: (none) */
#define  PAN_MAIN_LED_4                   29      /* control type: LED, callback function: (none) */
#define  PAN_MAIN_LED_5                   30      /* control type: LED, callback function: (none) */
#define  PAN_MAIN_LED_6                   31      /* control type: LED, callback function: (none) */
#define  PAN_MAIN_LED_7                   32      /* control type: LED, callback function: (none) */
#define  PAN_MAIN_LED_8                   33      /* control type: LED, callback function: (none) */
#define  PAN_MAIN_LED_9                   34      /* control type: LED, callback function: (none) */
#define  PAN_MAIN_LED_10                  35      /* control type: LED, callback function: (none) */
#define  PAN_MAIN_LED_11                  36      /* control type: LED, callback function: (none) */
#define  PAN_MAIN_NUM_TEMP                37      /* control type: numeric, callback function: (none) */
#define  PAN_MAIN_NUM_DEVIATION           38      /* control type: numeric, callback function: (none) */
#define  PAN_MAIN_NUM_ENC                 39      /* control type: numeric, callback function: (none) */
#define  PAN_MAIN_NUM_XACT                40      /* control type: numeric, callback function: (none) */
#define  PAN_MAIN_NUM_XTARGET             41      /* control type: numeric, callback function: (none) */
#define  PAN_MAIN_NUM_VELOCITY            42      /* control type: scale, callback function: cb_Velocity */
#define  PAN_MAIN_TEXTMSG_2               43      /* control type: textMsg, callback function: (none) */
#define  PAN_MAIN_DECORATION_3            44      /* control type: deco, callback function: (none) */
#define  PAN_MAIN_DECORATION_4            45      /* control type: deco, callback function: (none) */
#define  PAN_MAIN_DECORATION_2            46      /* control type: deco, callback function: (none) */
#define  PAN_MAIN_DECORATION              47      /* control type: deco, callback function: (none) */
#define  PAN_MAIN_TEXTMSG_4               48      /* control type: textMsg, callback function: (none) */
#define  PAN_MAIN_TEXTMSG_7               49      /* control type: textMsg, callback function: (none) */
#define  PAN_MAIN_TEXTMSG_5               50      /* control type: textMsg, callback function: (none) */
#define  PAN_MAIN_TEXTMSG_6               51      /* control type: textMsg, callback function: (none) */
#define  PAN_MAIN_TEXTMSG_3               52      /* control type: textMsg, callback function: (none) */
#define  PAN_MAIN_RNG_SETTO               53      /* control type: ring, callback function: (none) */
#define  PAN_MAIN_STR_FILENAME            54      /* control type: string, callback function: (none) */
#define  PAN_MAIN_TIM_STATUS              55      /* control type: timer, callback function: cb_StatusTimer */


     /* Control Arrays: */

          /* (no control arrays in the resource file) */


     /* Menu Bars, Menus, and Menu Items: */

          /* (no menu bars in the resource file) */


     /* Callback Prototypes: */

int  CVICALLBACK cb_CheckError(int panel, int control, int event, void *callbackData, int eventData1, int eventData2);
int  CVICALLBACK cb_Clear(int panel, int control, int event, void *callbackData, int eventData1, int eventData2);
int  CVICALLBACK cb_Close(int panel, int control, int event, void *callbackData, int eventData1, int eventData2);
int  CVICALLBACK cb_Config(int panel, int control, int event, void *callbackData, int eventData1, int eventData2);
int  CVICALLBACK cb_Disable(int panel, int control, int event, void *callbackData, int eventData1, int eventData2);
int  CVICALLBACK cb_Enable(int panel, int control, int event, void *callbackData, int eventData1, int eventData2);
int  CVICALLBACK cb_FileLoad(int panel, int control, int event, void *callbackData, int eventData1, int eventData2);
int  CVICALLBACK cb_FileSave(int panel, int control, int event, void *callbackData, int eventData1, int eventData2);
int  CVICALLBACK cb_motorParam(int panel, int control, int event, void *callbackData, int eventData1, int eventData2);
int  CVICALLBACK cb_Position(int panel, int control, int event, void *callbackData, int eventData1, int eventData2);
int  CVICALLBACK cb_remoteParam(int panel, int control, int event, void *callbackData, int eventData1, int eventData2);
int  CVICALLBACK cb_SetPosition(int panel, int control, int event, void *callbackData, int eventData1, int eventData2);
int  CVICALLBACK cb_StatusTimer(int panel, int control, int event, void *callbackData, int eventData1, int eventData2);
int  CVICALLBACK cb_Stop(int panel, int control, int event, void *callbackData, int eventData1, int eventData2);
int  CVICALLBACK cb_Velocity(int panel, int control, int event, void *callbackData, int eventData1, int eventData2);
int  CVICALLBACK cbDirectCommand(int panel, int control, int event, void *callbackData, int eventData1, int eventData2);


#ifdef __cplusplus
    }
#endif

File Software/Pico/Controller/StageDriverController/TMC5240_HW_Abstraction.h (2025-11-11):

#include <Arduino.h>

/*******************************************************************************
* Copyright © 2019 TRINAMIC Motion Control GmbH & Co. KG
* (now owned by Analog Devices Inc.),
*
* Copyright © 2023 Analog Devices Inc. All Rights Reserved.
* This software is proprietary to Analog Devices, Inc. and its licensors.
*******************************************************************************/

#ifndef TMC5240_HW_ABSTRACTION
#define TMC5240_HW_ABSTRACTION

//constants

#define TMC5240_REGISTER_COUNT   128
#define TMC5240_MOTORS           1
#define TMC5240_WRITE_BIT            0x80
#define TMC5240_ADDRESS_MASK         0x7F
#define TMC5240_MAX_VELOCITY     8388096
#define TMC5240_MAX_ACCELERATION u16_MAX
#define DEFAULT_ICID            0

// ramp modes (Register TMC5240_RAMPMODE)
#define TMC5240_MODE_POSITION  0
#define TMC5240_MODE_VELPOS    1
#define TMC5240_MODE_VELNEG    2
#define TMC5240_MODE_HOLD      3

// limit switch mode bits (Register TMC5240_SWMODE)
#define TMC5240_SW_STOPL_ENABLE    0x0001
#define TMC5240_SW_STOPR_ENABLE    0x0002
#define TMC5240_SW_STOPL_POLARITY  0x0004
#define TMC5240_SW_STOPR_POLARITY  0x0008
#define TMC5240_SW_SWAP_LR         0x0010
#define TMC5240_SW_LATCH_L_ACT     0x0020
#define TMC5240_SW_LATCH_L_INACT   0x0040
#define TMC5240_SW_LATCH_R_ACT     0x0080
#define TMC5240_SW_LATCH_R_INACT   0x0100
#define TMC5240_SW_LATCH_ENC       0x0200
#define TMC5240_SW_SG_STOP         0x0400
#define TMC5240_SW_SOFTSTOP        0x0800

// Status bits (Register TMC5240_RAMPSTAT)
#define TMC5240_RS_STOPL          0x0001
#define TMC5240_RS_STOPR          0x0002
#define TMC5240_RS_LATCHL         0x0004
#define TMC5240_RS_LATCHR         0x0008
#define TMC5240_RS_EV_STOPL       0x0010
#define TMC5240_RS_EV_STOPR       0x0020
#define TMC5240_RS_EV_STOP_SG     0x0040
#define TMC5240_RS_EV_POSREACHED  0x0080
#define TMC5240_RS_VELREACHED     0x0100
#define TMC5240_RS_POSREACHED     0x0200
#define TMC5240_RS_VZERO          0x0400
#define TMC5240_RS_ZEROWAIT       0x0800
#define TMC5240_RS_SECONDMOVE     0x1000
#define TMC5240_RS_SG             0x2000

// Encoderbits (Register TMC5240_ENCMODE)
#define TMC5240_EM_DECIMAL     0x0400
#define TMC5240_EM_LATCH_XACT  0x0200
#define TMC5240_EM_CLR_XENC    0x0100
#define TMC5240_EM_NEG_EDGE    0x0080
#define TMC5240_EM_POS_EDGE    0x0040
#define TMC5240_EM_CLR_ONCE    0x0020
#define TMC5240_EM_CLR_CONT    0x0010
#define TMC5240_EM_IGNORE_AB   0x0008
#define TMC5240_EM_POL_N       0x0004
#define TMC5240_EM_POL_B       0x0002
#define TMC5240_EM_POL_A       0x0001

// Registers in TMC5240
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
